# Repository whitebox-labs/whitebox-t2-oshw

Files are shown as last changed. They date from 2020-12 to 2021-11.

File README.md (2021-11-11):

model `T2.21 SMA`
# Whitebox T2 Mini MkII for Arduino

## Hardware repository

The Whitebox T2 Mini MkII is an Arduino Shield to easily connect and isolate Atlas Scientific EZO devices to an Arduino. The Whitebox T2 is Open Source Hardware and this is the public repository of the source files.

- Whitebox T2 user documentation: https://www.whiteboxes.ch/docs/tentacle/t2-mkII/#/
- Buy the Whitebox T2 here: https://www.whiteboxes.ch/shop/t2-mini-mk2/

Hardware source files licensed under [Creative Commons BY-SA 4.0](http://creativecommons.org/licenses/by-sa/4.0/)

Made with KiCAD logo (http://kicad.org/)

The Whitebox T2 Mini MkII hardware source is licensed under a
[Creative Commons Attribution-ShareAlike 4.0 International License][cc-by-sa].

[][cc-by-sa]

[cc-by-sa]: http://creativecommons.org/licenses/by-sa/4.0/
[cc-by-sa-image]: https://licensebuttons.net/l/by-sa/4.0/88x31.png

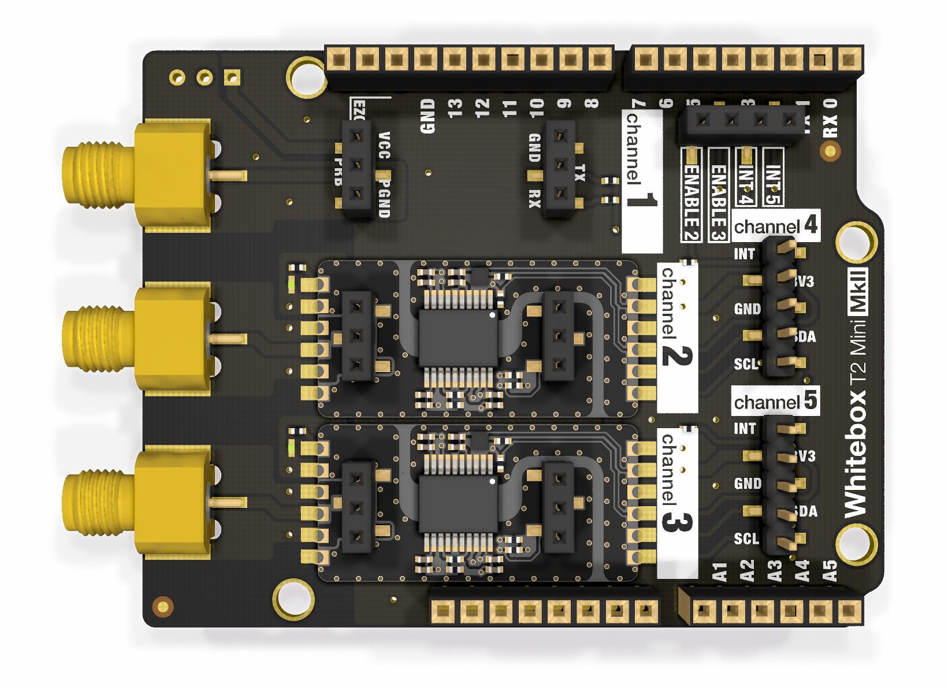
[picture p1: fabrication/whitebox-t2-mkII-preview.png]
Whitebox T2 Mini MkII


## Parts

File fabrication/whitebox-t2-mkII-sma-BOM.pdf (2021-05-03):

Whitebox T2 MkII SMA | 05 / 2021
| U201 U202 | 2 | tentacle:WB-T0-isolator
| D201 D202 | 2 20mA | tentacle:WB-LED-G-SMD-0402
| R101 R102 | 2 4.7K | tentacle:WB-R-SMD-0402
| R103 R104 | 2 1M | tentacle:WB-R-SMD-0402
| R201 R202 | 2 270 | tentacle:WB-R-SMD-0402
SMD connector for EZO | STP301 | 2 1x3 pin | tentacle:WB-EZO-RL
SMA connector | P201 P202 P301 | 3 SMA | tentacle:WB-SMA_EDGES_CORNER
| P102 | 1 1x4 pin | tentacle:WB-1x4-header-female-SMD
| P302 P303 | 2 1x5 pin | tentacle:WB-1x5-header-male-SMD
| SHIELD101 | 1 0.1” | tentacle-mini:WB-t2-shield
| SHIELD101 | 2 0.1” | tentacle-mini:WB-t2-shield
| SHIELD101 | 1 0.1” | tentacle-mini:WB-t2-shield
Description | Reference | Qty Value | Footprint
T0 Whitebox Isolator
LED for T0 Whitebox Isolator “on”
Resistor Size 0402, 1%, 1/8W (i2c)
Resistor Size 0402, 1%, 1/8W (enable) Resistor Size 0402, 1%, 1/16W (LED)

SMD female connector for disable
SMD male connector for channels 4 and 5 1x6-pin female header .1inch THT 1x8-pin female header .1inch THT 1x10-pin female header .1inch THT

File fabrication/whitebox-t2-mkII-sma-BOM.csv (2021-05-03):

Description | Reference | Qty | Value | Footprint
T0 Whitebox Isolator | U201 U202 | 2 |  | tentacle:WB-T0-isolator
LED for T0 Whitebox Isolator “on” | D201 D202 | 2 | 20mA | tentacle:WB-LED-G-SMD-0402
Resistor Size 0402, 1%, 1/8W (i2c) | R101 R102 | 2 | 4.7K | tentacle:WB-R-SMD-0402
Resistor Size 0402, 1%, 1/8W (enable) | R103 R104 | 2 | 1M | tentacle:WB-R-SMD-0402
Resistor Size 0402, 1%, 1/16W (LED) | R201 R202 | 2 | 270 | tentacle:WB-R-SMD-0402
SMD connector for EZO | STP301 | 2 | 1x3 pin | tentacle:WB-EZO-RL
SMA connector | P201 P202 P301 | 3 | SMA | tentacle:WB-SMA_EDGES_CORNER
SMD female connector for disable | P102 | 1 | 1x4 pin | tentacle:WB-1x4-header-female-SMD
SMD male connector for channels 4 and 5 | P302 P303 | 2 | 1x5 pin | tentacle:WB-1x5-header-male-SMD
1x6-pin female header .1inch THT | SHIELD101 | 1 | 0.1” | tentacle-mini:WB-t2-shield
1x8-pin female header .1inch THT | SHIELD101 | 2 | 0.1” | tentacle-mini:WB-t2-shield
1x10-pin female header .1inch THT | SHIELD101 | 1 | 0.1” | tentacle-mini:WB-t2-shield

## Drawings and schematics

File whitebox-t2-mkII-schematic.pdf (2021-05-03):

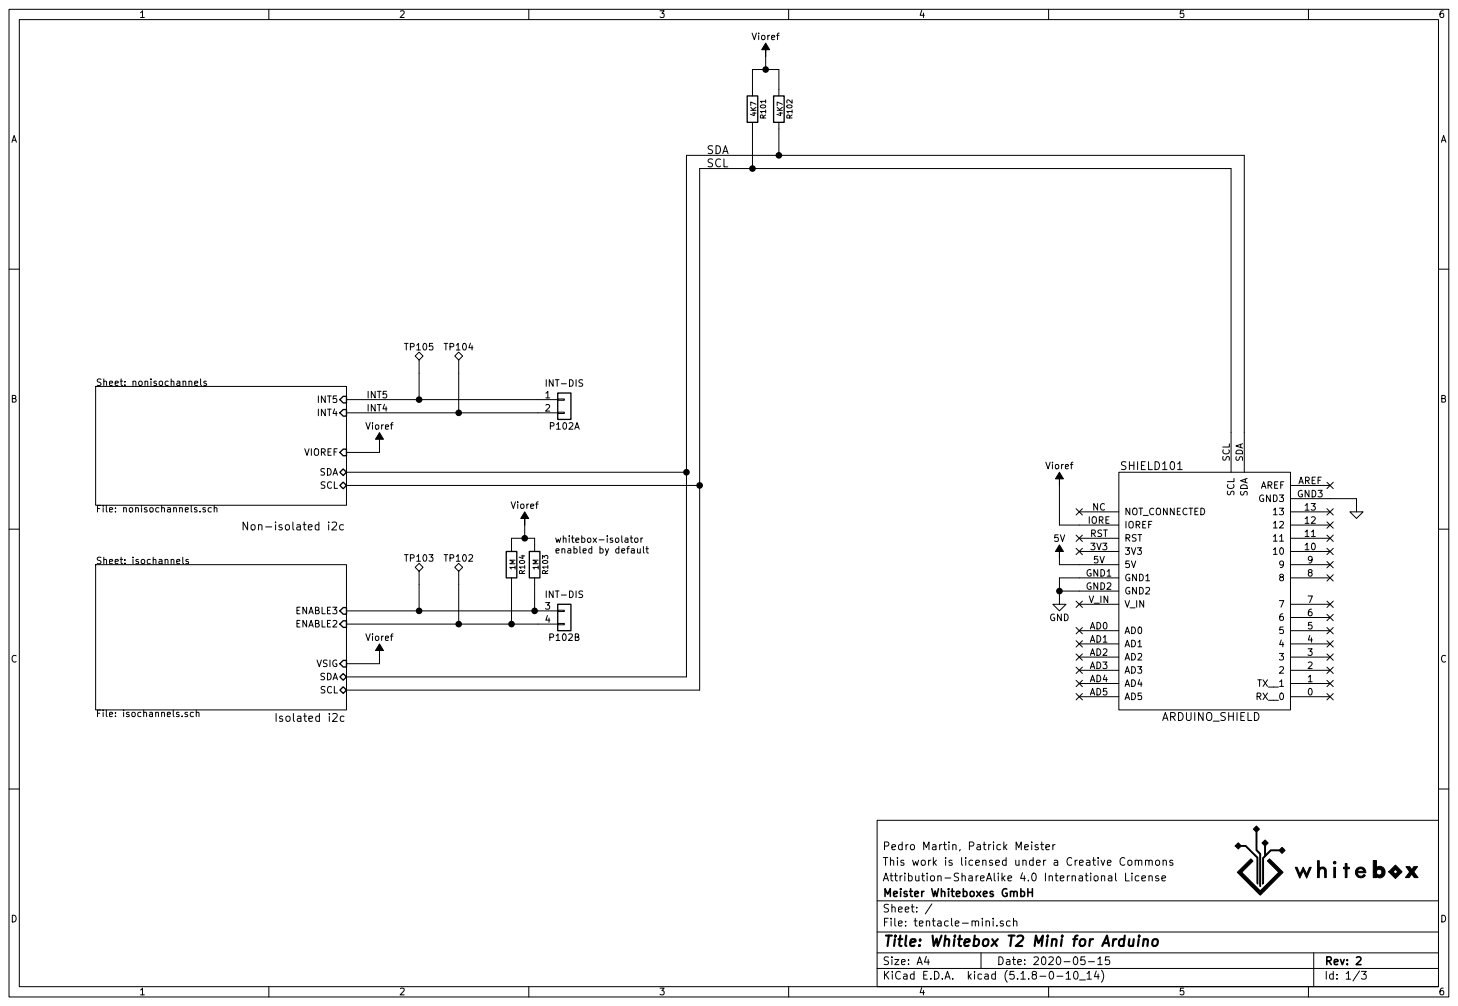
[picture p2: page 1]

SCL whitebox-isolator enabled by default Isolated i2c Non-isolated i2c

Attribution-ShareAlike 4.0 International License This work is licensed under a Creative Commons Pedro Martin, Patrick Meister

File: tentacle-mini.sch Sheet: / Meister Whiteboxes GmbH

Id: 1/3 Title: Whitebox T2 Mini for Arduino

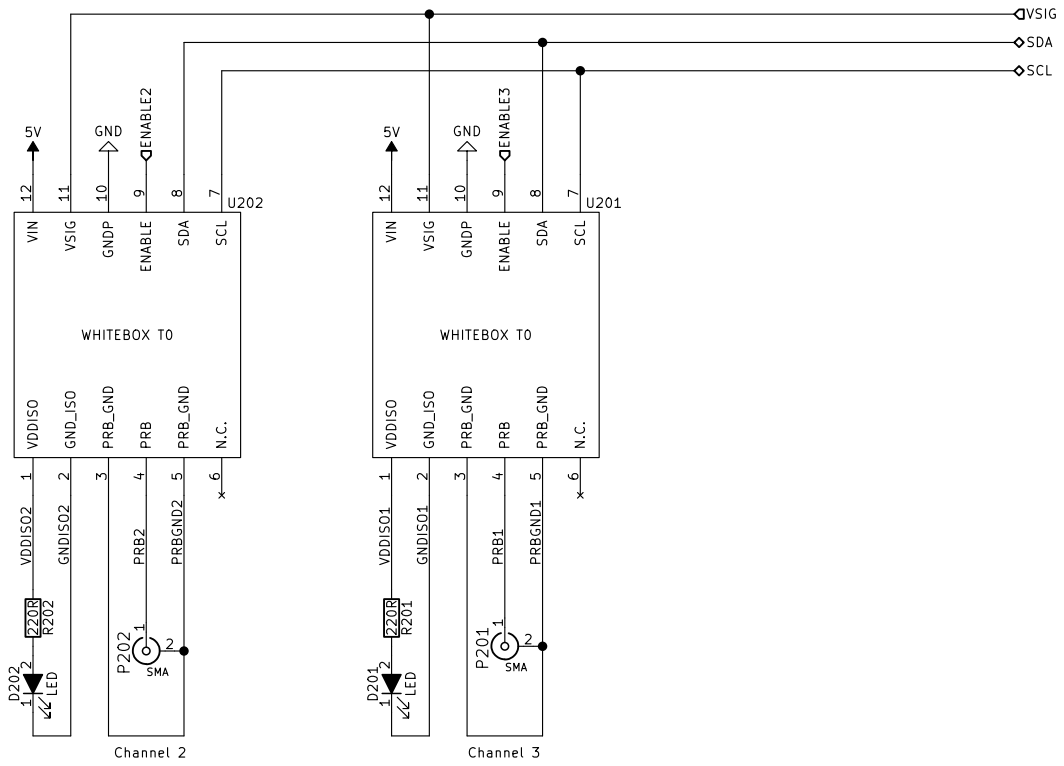
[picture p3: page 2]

9 U201 WHITEBOX T0 VSIG ENABLE2 ENABLE3 SCL SDA VDDISO2 GNDISO2 PRB2 PRBGND2 VDDISO1 GNDISO1 PRB1 PRBGND1 Channel 2 Channel 3

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

File: isochannels.sch Sheet: /isochannels/ Meister Whiteboxes GmbH

Id: 2/3 Title: Whitebox T2 Mini for Arduino

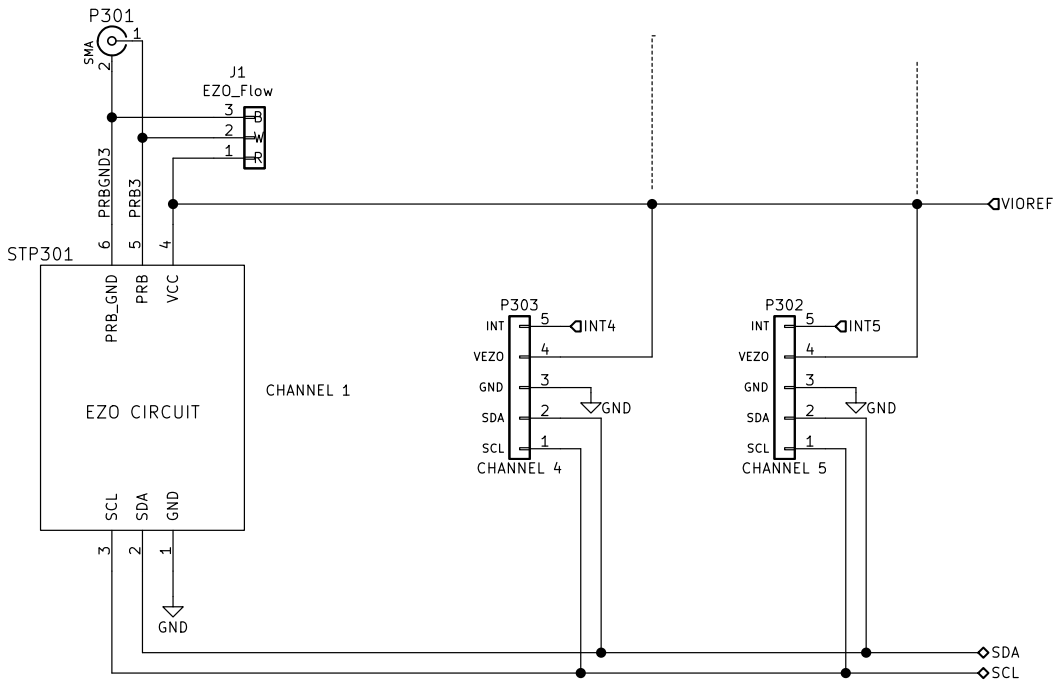
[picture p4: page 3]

Attribution-ShareAlike 4.0 International License This work is licensed under a Creative Commons Pedro Martin, Patrick Meister GND

File: nonisochannels.sch Sheet: /nonisochannels/ Meister Whiteboxes GmbH

Id: 3/3 Title: Whitebox T2 Mini for Arduino

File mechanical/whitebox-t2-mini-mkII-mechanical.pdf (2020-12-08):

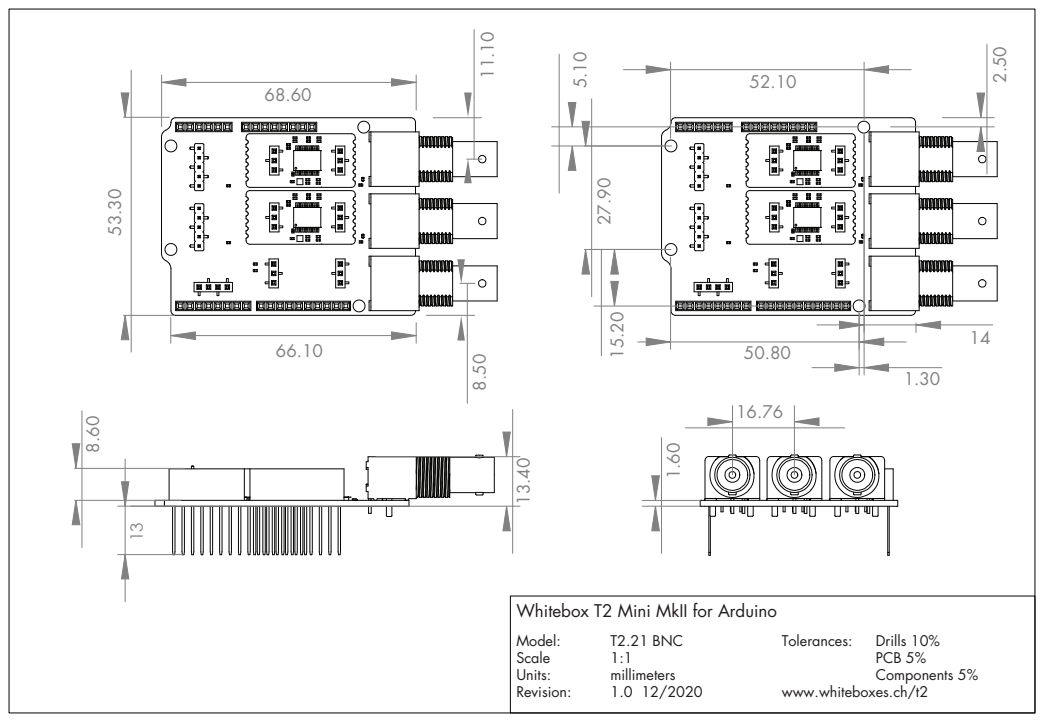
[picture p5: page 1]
Tolerances:; Drills 10%; PCB 5% Components 5%; Model:; T2.21 BNC; Scale; Units:; millimeters; Revision:

Whitebox T2 Mini MkII for Arduino

www.whiteboxes.ch/t2

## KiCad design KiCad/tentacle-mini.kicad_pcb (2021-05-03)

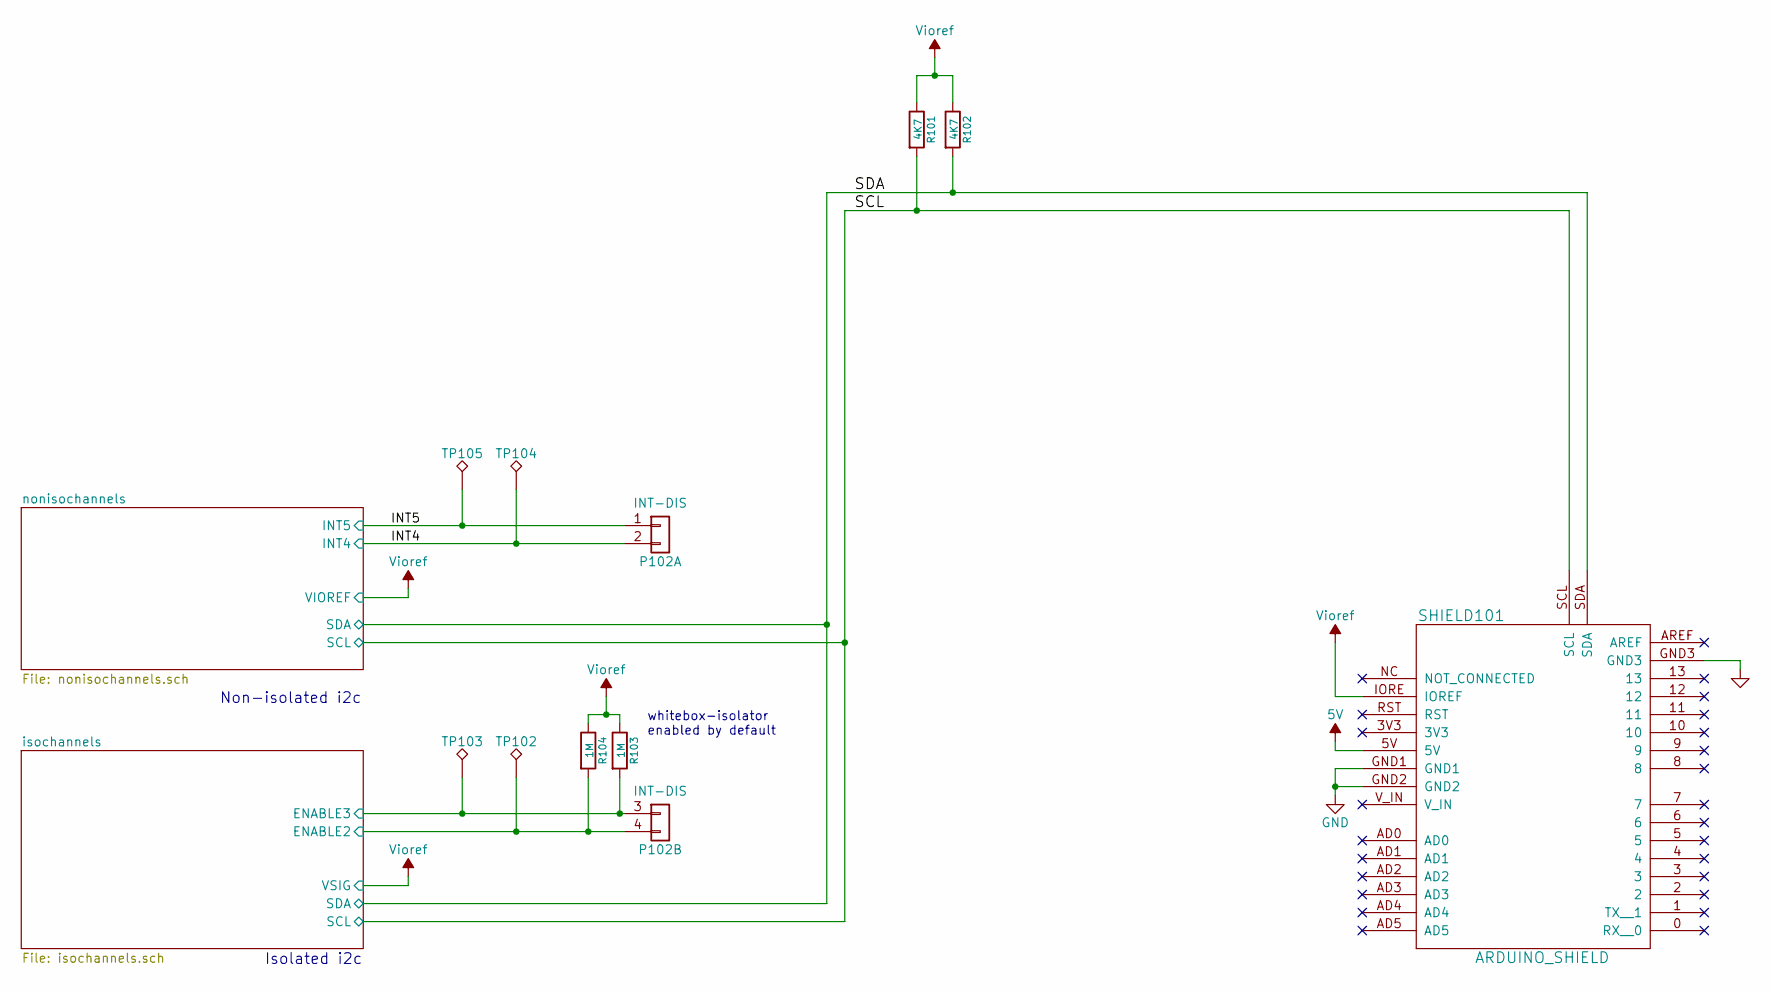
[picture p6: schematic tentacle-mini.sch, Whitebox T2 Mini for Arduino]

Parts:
P102: INT-DIS; WB-1x4-header-female-SMD
R101, R102: 4K7; WB-R-SMD-0402
R103, R104: 1M; WB-R-SMD-0402
SHIELD101: ARDUINO_SHIELD; WB-t2-shield
TP102, TP103, TP104, TP105: TestPoint; WB-testpoint

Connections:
5V: SHIELD101.5V; also elsewhere on the board
/INT4: P102.2 (Pin_4), TP104.1; also elsewhere on the board
/INT5: P102.1 (Pin_3), TP105.1; also elsewhere on the board
/SCL: R101.2, SHIELD101.SCL; also elsewhere on the board
/SDA: R102.2, SHIELD101.SDA; also elsewhere on the board
/isochannels/ENABLE2: P102.4, R104.2, TP102.1; also elsewhere on the board
/isochannels/ENABLE3: P102.3, R103.2, TP103.1; also elsewhere on the board
GND: SHIELD101.GND1, SHIELD101.GND2, SHIELD101.GND3; also elsewhere on the board
Vioref: R101.1, R102.1, R103.1, R104.1, SHIELD101.IORE (IOREF); also elsewhere on the board

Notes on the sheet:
Non-isolated i2c
Isolated i2c
whitebox-isolator enabled by default

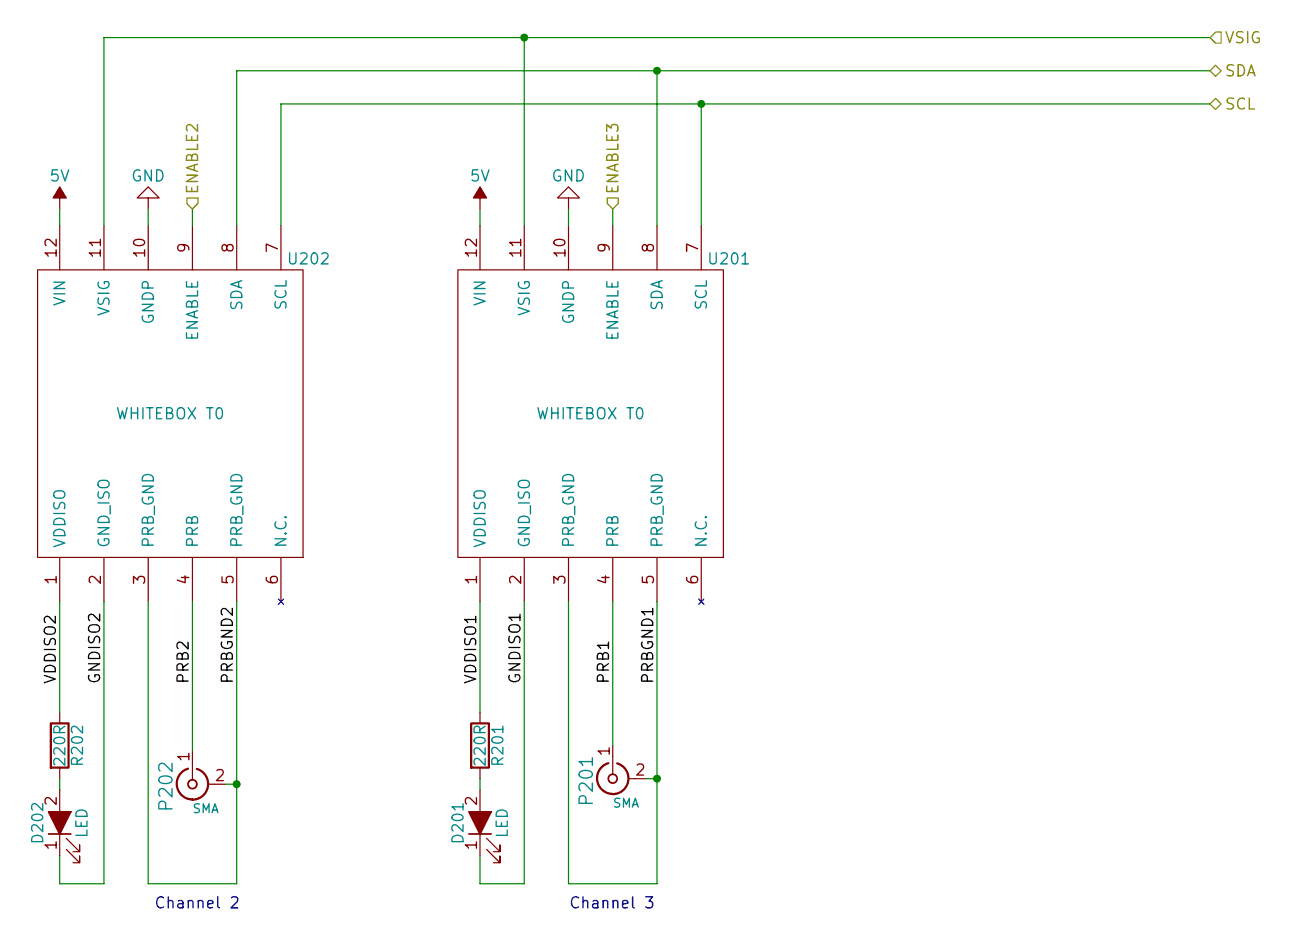
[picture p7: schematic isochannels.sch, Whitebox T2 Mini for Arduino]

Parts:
D201, D202: LED; WB-LED-G-SMD-0402
P201, P202: SMA; WB-SMA_EDGES_CORNER
R201, R202: 220R; WB-R-SMD-0402
U201, U202: WHITEBOX T0; WB-T0-isolator-temporary-bugfix

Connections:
5V: U201.12 (VIN), U202.12 (VIN); also elsewhere on the board
/SCL: U201.7 (SCL), U202.7 (SCL); also elsewhere on the board
/SDA: U201.8 (SDA), U202.8 (SDA); also elsewhere on the board
/isochannels/ENABLE2: U202.9 (ENABLE); also elsewhere on the board
/isochannels/ENABLE3: U201.9 (ENABLE); also elsewhere on the board
/isochannels/GNDISO1: D201.1 (K), U201.2 (GND_ISO)
/isochannels/GNDISO2: D202.1 (K), U202.2 (GND_ISO)
/isochannels/PRB1: P201.1 (In), U201.4 (PRB)
/isochannels/PRB2: P202.1 (In), U202.4 (PRB)
/isochannels/PRBGND1: P201.2 (Ext), U201.3 (PRB_GND), U201.5 (PRB_GND)
/isochannels/PRBGND2: P202.2 (Ext), U202.3 (PRB_GND), U202.5 (PRB_GND)
/isochannels/VDDISO1: R201.1, U201.1 (VDDISO)
/isochannels/VDDISO2: R202.1, U202.1 (VDDISO)
GND: U201.10 (GNDP), U202.10 (GNDP); also elsewhere on the board
unnamed: D201.2 (A), R201.2
unnamed: D202.2 (A), R202.2
Vioref: U201.11 (VSIG), U202.11 (VSIG); also elsewhere on the board

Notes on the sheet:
Channel 3
Channel 2

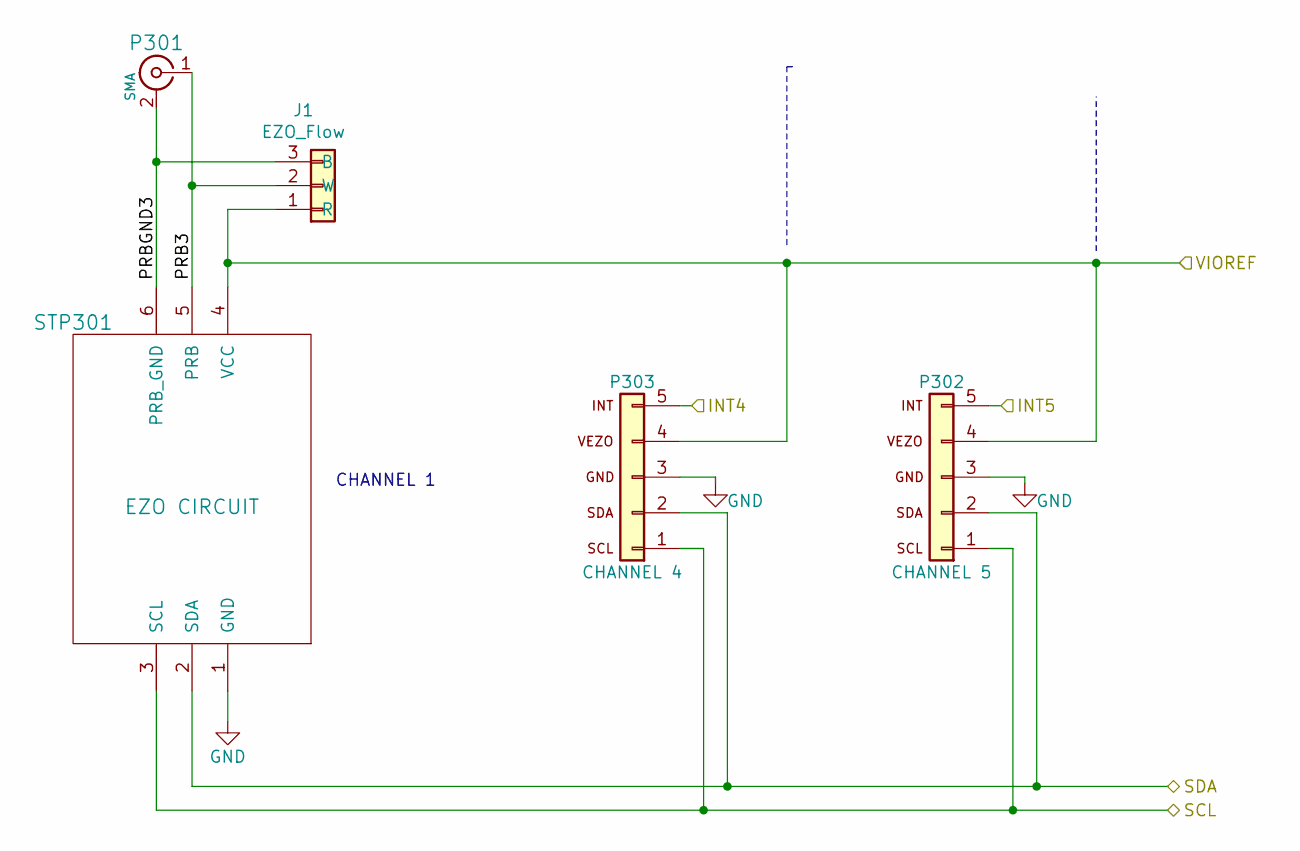
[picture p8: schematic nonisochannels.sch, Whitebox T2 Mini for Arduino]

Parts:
J1: EZO_Flow; WB-1x3-pin-header-handsolder
P301: SMA; WB-SMA_EDGES_CORNER
P302: CHANNEL 5; WB-1x5-header-male-SMD
P303: CHANNEL 4; WB-1x5-header-male-SMD
STP301: EZO CIRCUIT; WB-EZO-RL

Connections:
/INT4: P303.5; also elsewhere on the board
/INT5: P302.5; also elsewhere on the board
/SCL: P302.1, P303.1, STP301.3 (SCL); also elsewhere on the board
/SDA: P302.2, P303.2, STP301.2 (SDA); also elsewhere on the board
/nonisochannels/PRB3: J1.2 (W), P301.1 (In), STP301.5 (PRB)
/nonisochannels/PRBGND3: J1.3 (B), P301.2 (Ext), STP301.6 (PRB_GND)
GND: P302.3, P303.3, STP301.1 (GND); also elsewhere on the board
Vioref: J1.1 (R), P302.4, P303.4, STP301.4 (VCC); also elsewhere on the board

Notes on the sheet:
CHANNEL 1

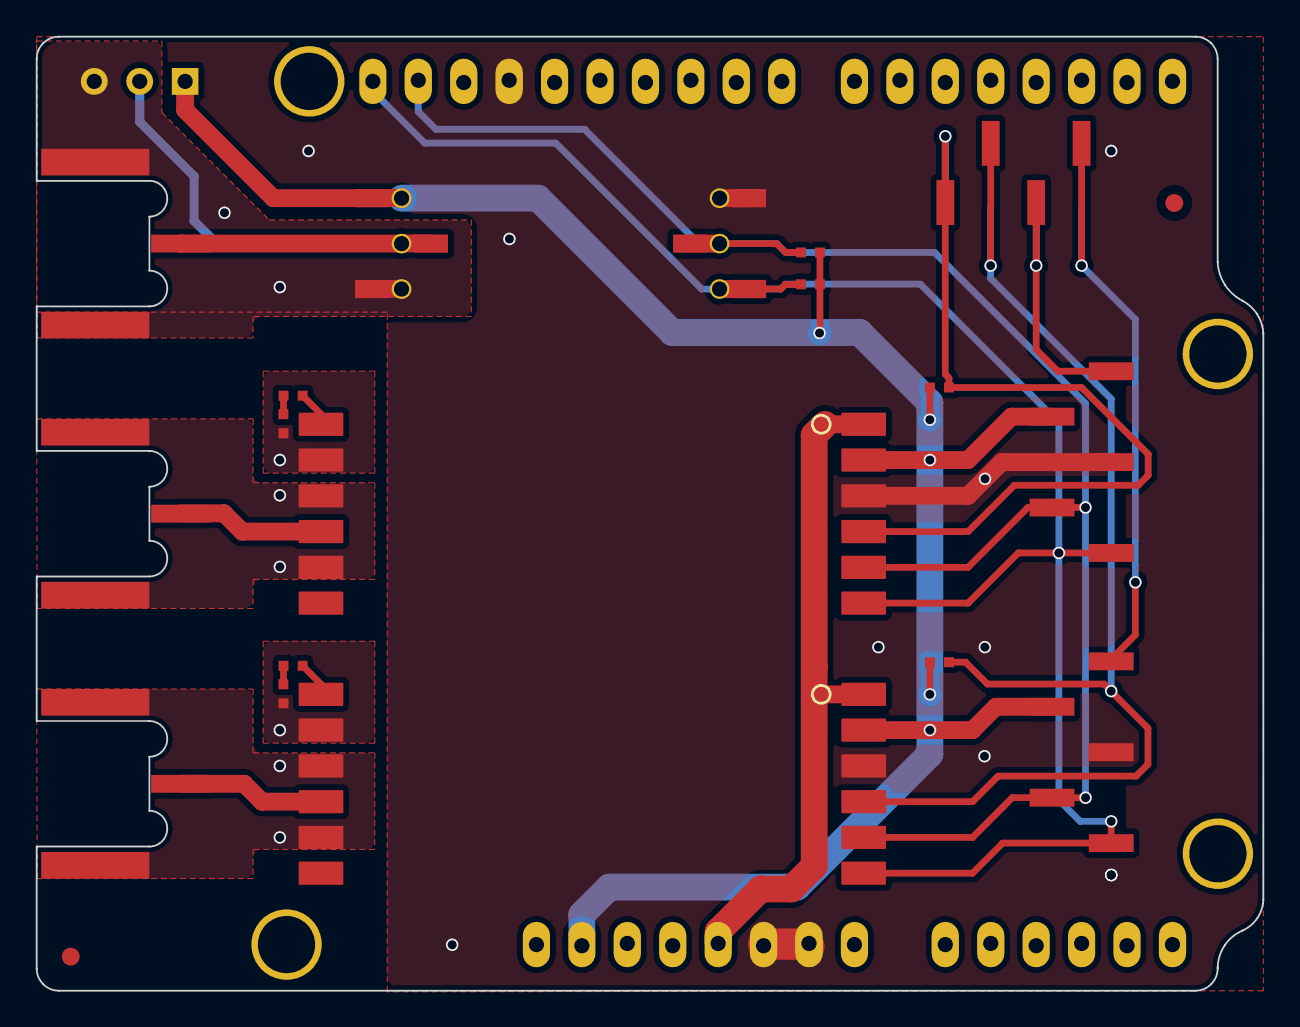
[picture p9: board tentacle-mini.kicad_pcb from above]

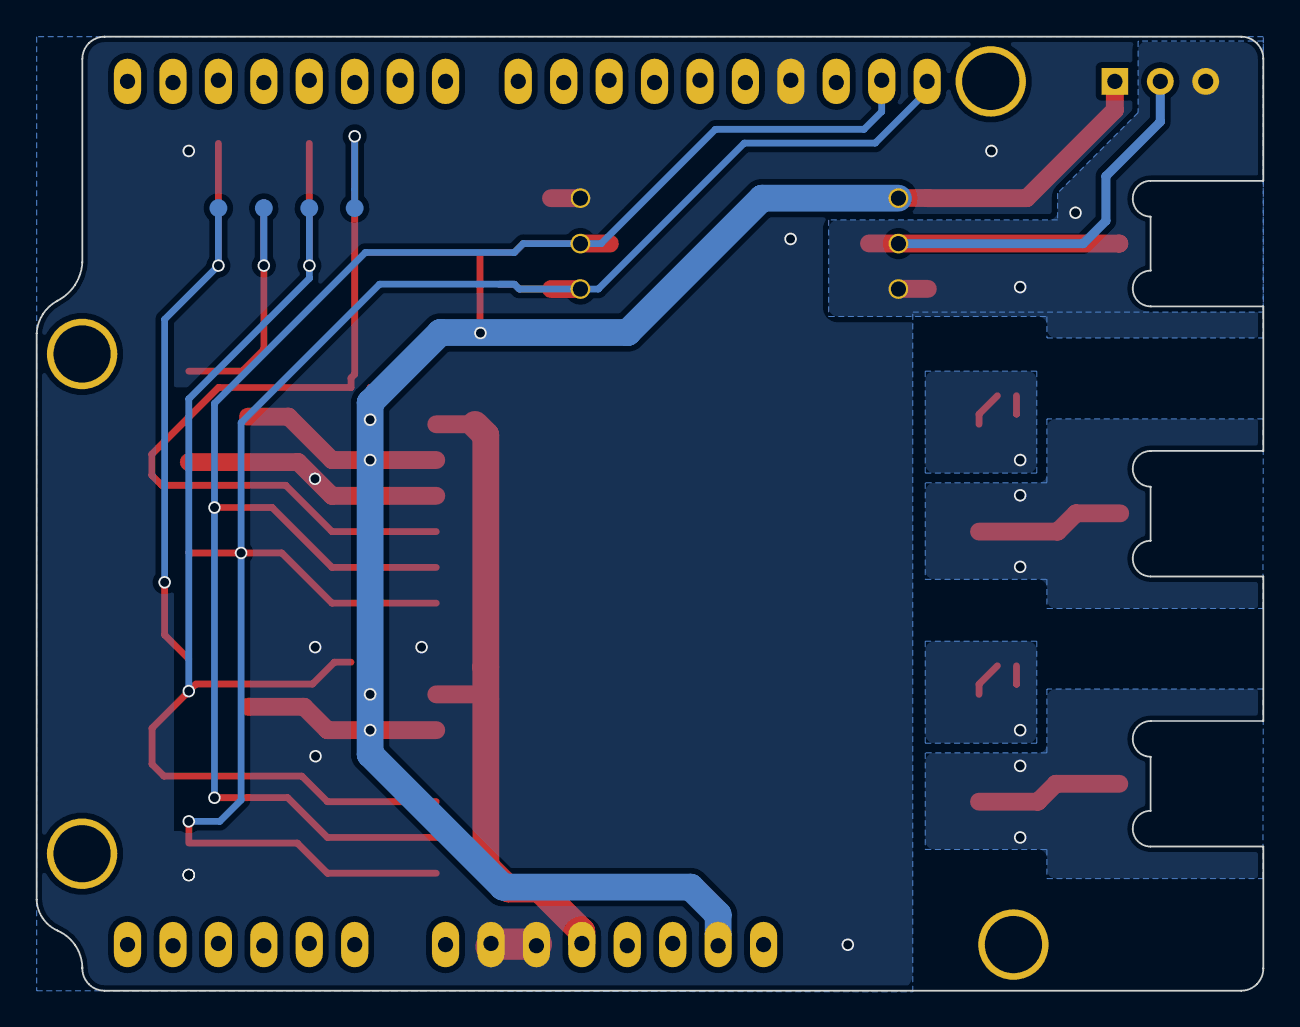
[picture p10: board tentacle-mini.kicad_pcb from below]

Board: 2 copper layers, 68.6 x 53.3 mm, 25 parts (4 on the bottom side), 21 nets.

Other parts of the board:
fiducial: FIDUCIAL 1; WB-fiducial_1mm
fiducial#2: FIDUCIAL 2; WB-fiducial_1mm

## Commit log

2020-12-08 added whitebox t2 mkII hardware source files
    [isochannels.sch, nonisochannels.sch, tentacle-mini.kicad_pcb, tentacle-mini.sch]
2020-12-08 added BOM in csv format + zipped STEP file
    [whitebox-t2-bom.csv]
2021-05-03 updated bom, preview, readme, schematic pdf for SMA
    [whitebox-t2-mkII-sma-BOM.csv, whitebox-t2-mkII-sma-BOM.ods]
2021-05-03 update for SMA
    [isochannels.sch, nonisochannels.sch, tentacle-mini.kicad_pcb, tentacle-mini.sch]
2021-11-10 Update README.md
    https://forum.kicad.info/t/warning-avoid-all-links-to-kicad-pcb-org-use-kicad-org/31521

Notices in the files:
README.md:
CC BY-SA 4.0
